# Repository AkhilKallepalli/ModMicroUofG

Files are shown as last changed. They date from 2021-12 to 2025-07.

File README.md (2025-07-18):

# **ModMicroUofG**

<p align="center">
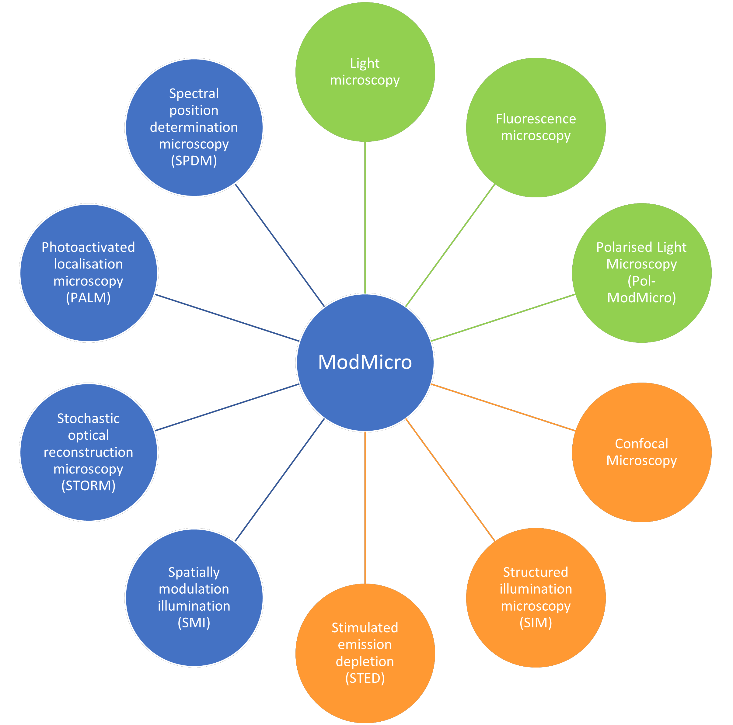
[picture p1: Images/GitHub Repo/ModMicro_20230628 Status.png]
ModMicro Status Update

</p>

**Mod**ular **Micro**scopy is an ongoing project, focusing on building low-cost and accessible hardware for realising standard and complex microscopic techniques. The repository contains all the files, modifications and updates.

<p align="center">
Work in Progress Logo
</p> 

---

# **Contents**

## **Phase 1: [OpenFlexure microscope](https://openflexure.org/) and machine learning-enhanced classification** 

The research adopts the OpenFlexure Delta Stage microscope (https://openflexure.org/) that allows motorised control and maximum stability of the samples when imaging. A Raspberry Pi camera is used for imaging the samples in a transmission-based illumination setup. The imaging data collected is catalogued and organised for classification using TensorFlow. Using visual interpretation, we have created subsets from amongst the samples to experiment for the best classification results. We found that by removing similar samples, the categorical accuracy achieved was 99.9% and 99.59% for the training and testing sets. Our research shows evidence of the efficacy of open source tools and methods. Future approaches will use improved resolution images for classification and other modalities of microscopy will be realised based on the OpenFlexure microscope. TEST

**Important Links**: 
- [GitHub](https://github.com/AkhilKallepalli/ModMicroUofG/tree/260d3f88ae4605c2fc237944587647aae78d652a/Phase%201%20(Microscope%20and%20ML))
- [OPEN-BIOset Dataset](http://dx.doi.org/10.5525/gla.researchdata.1149)
- SPIE Conference Proceeding: [Modular light sources for microscopy and beyond (ModLight)](https://doi.org/10.1117/12.2599435)

---
---

## **ModLight: Modular light sources** 

Modular light (ModLight) sources can be integrated into complex systems for microscopy, medical imaging, remote sensing, and so many more. Motivated by the need for affordable and open-access alternatives that are globally relevant, we have designed and shared light devices that use simple, off-the-shelf components. Red, green, blue, white and near-infrared LEDs are combined using mirrors and X-Cube prisms in novel devices. This modular nature allows portability and mounting flexibility. The ModLight suite can be used with any optical system that requires single- or multi-wavelength illumination such as bright-field and epifluorescence microscopes.

**Important Links**: 
- [Zenodo](https://zenodo.org/record/7385903)
- HardwareX Paper: [Modular light sources for microscopy and beyond (ModLight)](https://doi.org/10.1016/j.ohx.2022.e00385)

***NOTE**: Files of the same version as on Zenodo and HardwareX paper availble through this [GitHub Folder](https://github.com/AkhilKallepalli/ModMicroUofG/tree/c88cae8ca496235c1b51023b1f2a8044d0d7d9a2/ModLight).* 

---
---

## **Phase 2: Epifluorescence Microscopy** 

In collaboration with [Dr Jonathan Taylor](https://www.gla.ac.uk/schools/physics/staff/jonathantaylor/), the research led by Mr Robert Archibald investigated comparing a modular epifluorescence microscope with a standard Nikon Ti-Eclipse microscope. The results have shown that our results match the resolution and image sharpness as compared to a proprietary microscope, that latter costing many orders of the 3D printed microscopy system. 

### ***Hardware*** 
The original [OpenFlexure microscope](https://openflexure.org/) is adopted as the template, leveraging the flexures and their stability. Our contributions include a modified version of the epifluorescence setup to enhance access to the optics, introduce modular attachments and in-house built [ModLight](https://doi.org/10.1016/j.ohx.2022.e00385) sources to increase the spectral fidelity of a single system. 

### ***Sharpening Algorithm*** 
Image prossessing techniques are an essential step in data analysis, especially so when the image quality is degraded. This paper presents an iterative sharpening algorithm designed for use on the OpenFlexure Microscope, to bring z-stack images back into focus. Three different sharpness metrics are evaluated and the data needed to process these images, and establish the highest quality after image acquisition is available [here](https://github.com/AkhilKallepalli/ModMicroUofG/tree/a79b8e51664f305bbde2d7f3cc1418ee8469735c/Phase%202%20(Epifluorescence%20Microscope)/Sharpening%20algorithm). 

**Important Links**: 
- [GitHub](https://github.com/AkhilKallepalli/ModMicroUofG/tree/260d3f88ae4605c2fc237944587647aae78d652a/Phase%202%20(Epifluorescence%20Microscope))
- Research article: **Under Preparation**

---
---

## **Phase 3: Confocal Microscopy** 

<p align="center">
Work in Progress Logo
</p> 

---
---

## **Phase 4: Structured Illumination Microscopy** 

<p align="center">
Work in Progress Logo
</p> 

---
---

<p align="center">
     
</p>

---
---

## *Contact Information*

*For further details, discussions and collaborations, please contact Dr Akhil Kallepalli*\
**Email**: Akhil.Kallepalli@glasgow.ac.uk

*To learn more about our research, check out the lab website*\
**Website**: https://kallepallilab.com

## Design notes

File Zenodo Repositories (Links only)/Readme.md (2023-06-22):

# Zenodo Repositories 

Our research is currently distributed across Git and Zenodo repositories. While the Git repositories are accessible on [Github](https://github.com/AkhilKallepalli/ModMicroUofG), three repositories currently reside on Zenodo: 

- [**Biophotonics for All: Light Transport through Tissue**](https://zenodo.org/record/7876304)
- [**Pol-ModMicro**](https://zenodo.org/record/7837389)
- [**Modular light sources for microscopy and beyond (ModLight)**](https://zenodo.org/record/7385903)

---

## Biophotonics for All: Light transport through tissue

[Repository Access](https://zenodo.org/record/7876304)

This repository includes:

- Design files of electronics, mounts, LED Assembly (from ModLight) and LED mounts 
- Kit overview and LEDs assembly photographs 
- Demonstration Video of the Kit
- Bill of Materials

Biophotonics is becoming increasingly prominent in value and visibility. What was predominantly an advanced field of research is now being included increasingly in undergraduate and postgraduate programmes. To increase biophotonics-related STEM awareness, we developed simple and inexpensive LEDs and a camera set-up that allows visualising the blood vessels beneath the skin. The kit uses inexpensive blue, green, red and near-infrared LEDs to show the absorption of shorter wavelengths and transmission in the longer wavelengths in the finger. As an outreach and educational tool, this kit will illustrate the potential of using light for diagnostics.

<p align="center">
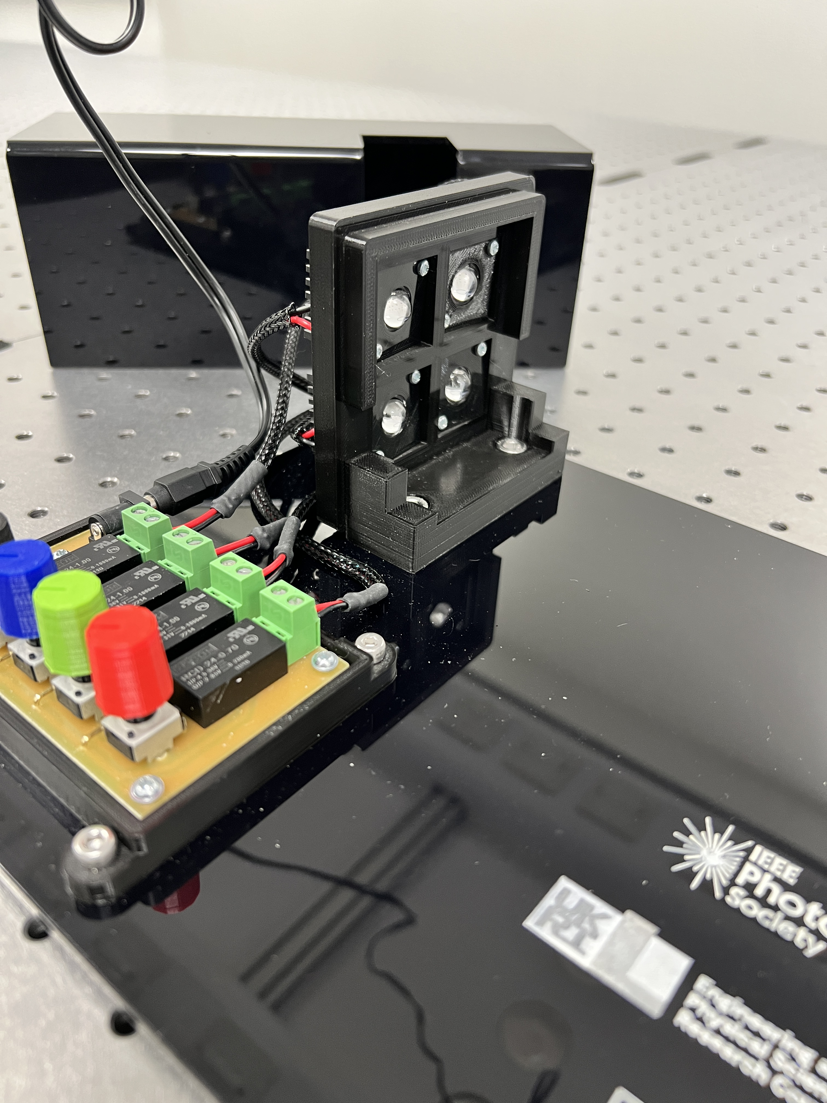
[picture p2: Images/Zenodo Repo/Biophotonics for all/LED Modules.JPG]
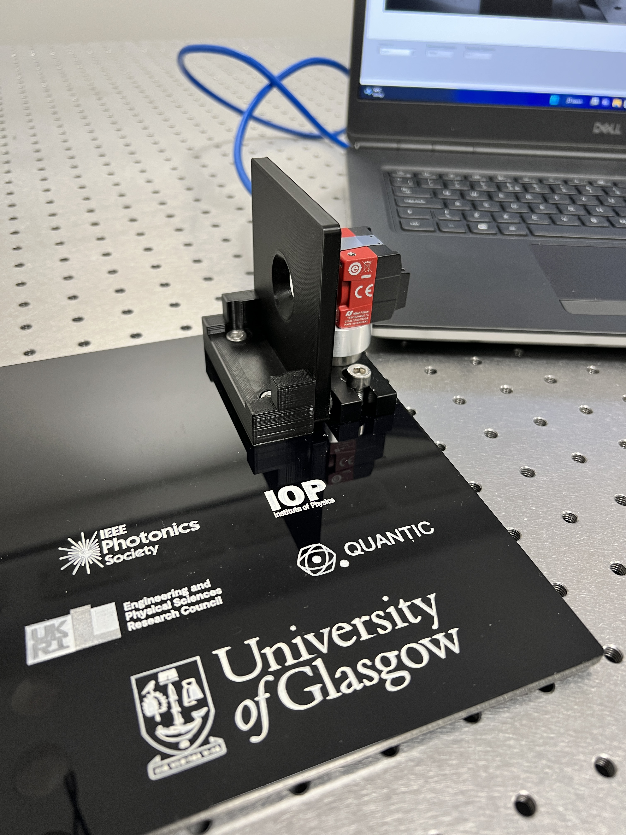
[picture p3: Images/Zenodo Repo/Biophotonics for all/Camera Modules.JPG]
 
</p>

<p align="center">

</p>

---

## Polarised light modular microscopy (Pol-ModMicro) for identifying hemozoin crystals in Plasmodium

[Repository Access](https://zenodo.org/record/7837389)

In this repository, you will find all the files needed to recreate the Pol-ModMicro system. These include: 

- Unmodified OpenFlexure files; as used in the system. 
- Modified/Updated Components to allow ModLight integration
- OpenFlexure Nano Motor Controller files
- Bill of Materials

Plasmodium spp. are the protozoan parasites responsible for malaria. Plasmodium spp. synthesise a biocrystal, hemozoin, which can be observed under cross-polarised light. These birefringent crystals can be seen due to different refractive indices of the hemozoin crystal and red blood cells. Here, we present a polarised light modular microscopy (Pol-ModMicro) solution, complete with illumination sources and a robust imaging system to capture birefringence and identify the parasites. We achieve this by combining ModLight light sources with bespoke components designed for the OpenFlexure microscope to image blood smears. Further, a simple and robust algorithm capable of enhancing birefringence is presented. This solution provides image quality that is comparable to a substantially more expensive proprietary microscope. 

<p align="center">
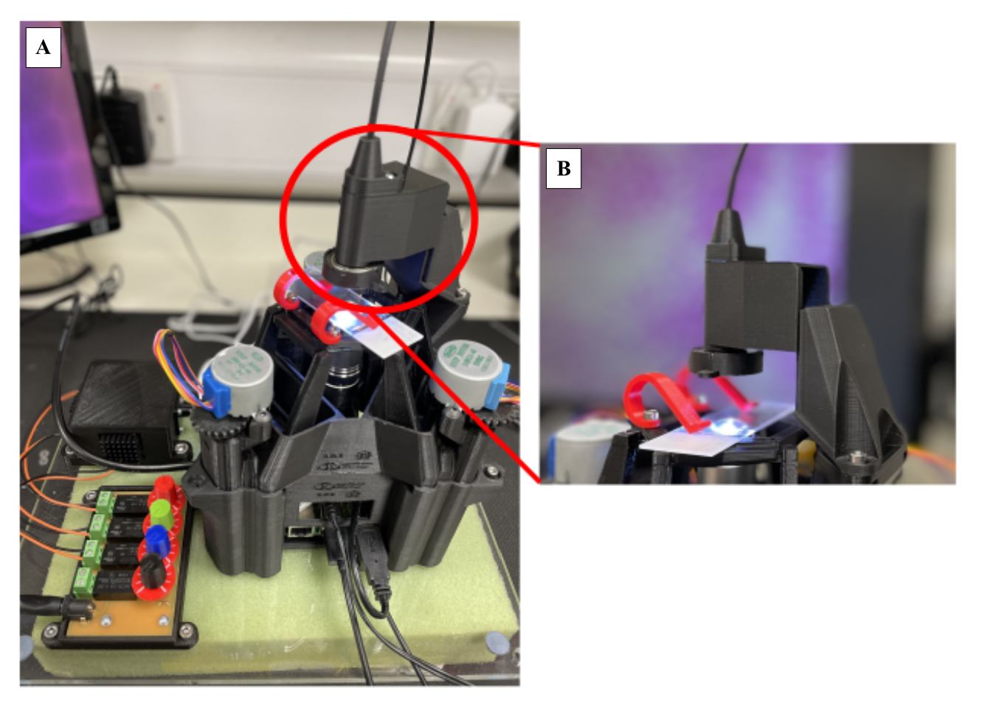
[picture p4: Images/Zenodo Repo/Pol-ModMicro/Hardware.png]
 
</p>

---

## Modular Light Sources for Microscopy and Beyond (ModLight)

[Repository Access](https://zenodo.org/record/7385903)

***NOTE**: Files of the same version as on Zenodo and HardwareX paper availble through this [GitHub Folder](https://github.com/AkhilKallepalli/ModMicroUofG/tree/c88cae8ca496235c1b51023b1f2a8044d0d7d9a2/ModLight).* 

Modular light (ModLight) sources can be integrated into complex systems for microscopy, medical imaging, remote sensing, and so many more. Motivated by the need for affordable and open-access alternatives that are globally relevant, we have designed and shared light devices that use simple, off-the-shelf components. Red, green, blue, white and near-infrared LEDs are combined using mirrors and X-Cube prisms in novel devices. This modular nature allows portability and mounting flexibility. The ModLight suite can be used with any optical system that requires single- or multi-wavelength illumination such as bright-field and epifluorescence microscopes.

<p align="center">
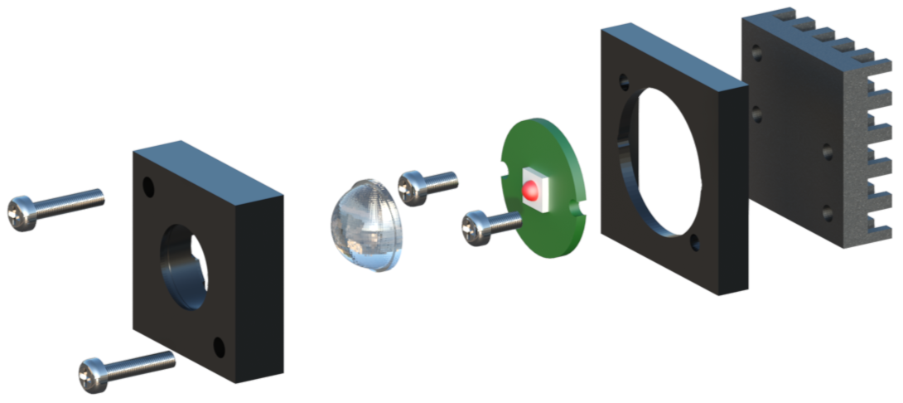
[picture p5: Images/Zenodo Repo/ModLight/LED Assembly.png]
  
</p>

<p align="center">
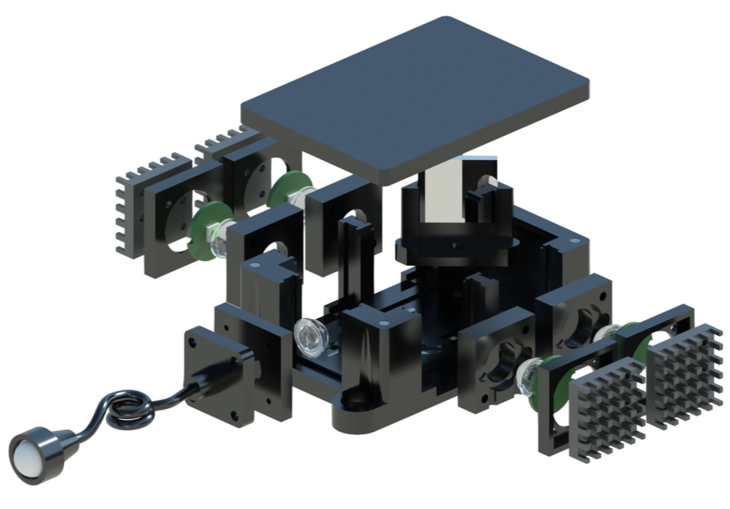
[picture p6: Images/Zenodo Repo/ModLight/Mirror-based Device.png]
 
</p>

<p align="center">
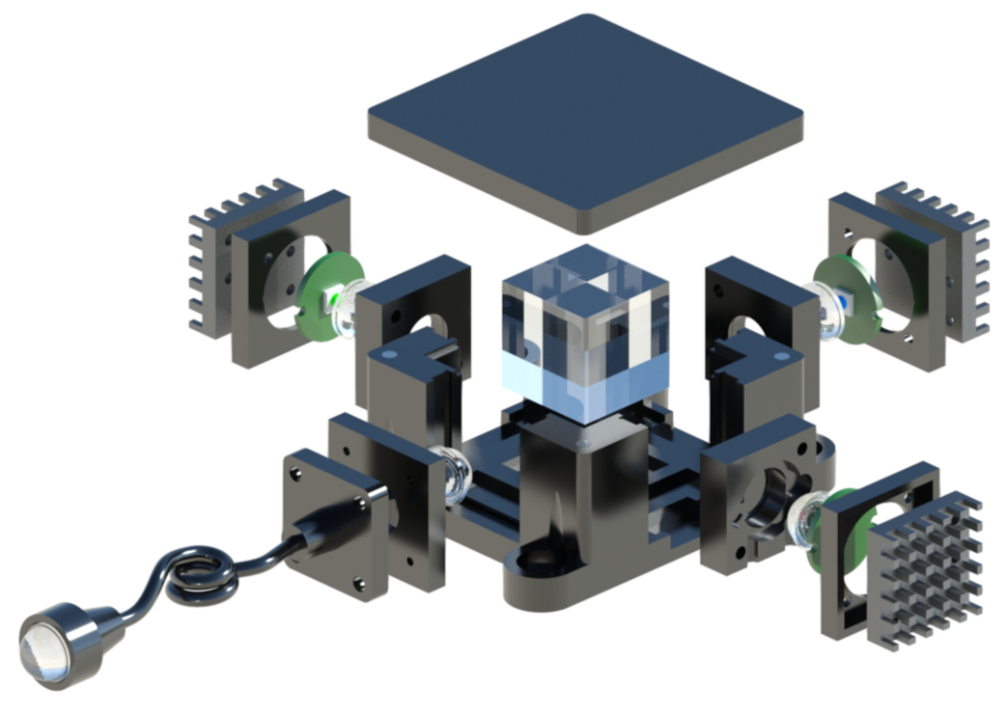
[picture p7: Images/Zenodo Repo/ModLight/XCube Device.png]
 
</p>

<p align="center">
 
</p>

---

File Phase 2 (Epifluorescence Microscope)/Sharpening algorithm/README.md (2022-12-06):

# Z-stack Image Sharpening Algorithm

---

## **Contact Information**

For further details on the algorithm, please contact Ms Harriet Bishop.\
Email: hattiebishop2@gmail.com\
LinkedIn: www.linkedin.com/in/harrietbishop

---

## **Contents**

Provided is a jupyter notebook (.ipynb) file containing an algorithm which sharpens z-stack images as well as the sample data used to test and build the algorithm. 

**The Algorithm:** The algorithm takes each image and sharpens it using various low pass filters. It then selects the optimal image by comparing the peaks in the pixel intensity produced when plotting a line across a prominent feature in the image.  It compares the full width half maximum of the images sharpened by each filter and finds the narrowest (and thus sharpest) one. The algorithm returns the optimized n value which relates to the most suitable low pass filter, of the form np.ones((n,n),np.float32)/(n^2) as well as the images sharpened using this filter. 

**Sample Data:** The sample data provided is a set of z-stack images of an Onion Epidermis slide, taken using the 3D printed OpenFlexure Microscope. The images depict different layers of the onion sample, with 200nm between each plane in the z-direction. The first half of the images (0-48) have been removed due to significant drift in the x-y axis. The starting image, Image 49, is the sharpest image in the stack having been taken at the focal point. The following images are increasingly blurred. Passing this dataset through the algorithm should return an n value of 5 along with a before and after of each image. 

---

## **Motivation**

Z-stack images are taken by adjusting the distance between the sample and the collection optics to focus on different layers of the image. As the sample is moved away from the focal plane, the image becomes increasingly blurred due to out of focus light reaching the collection optics. This algorithm provides a solution to partially restore these blurred images by removing low-frequency regions in the image, extracted using a low pass filter. Different sized filters are appropriate for different images, and this algorithm aims to find and apply the most appropriate filter given a set of images. 

---

## **User Inputs**

The algorithm must be provided with the below listed inputs. 

**directory:** The path to the folder with which the images are located.\
For example: *directory = '/Users/harrietbishop/My Project/Images/OnionEpidermis'*

**x1,y1,x2,y2:** The pixel coordinates plotting a line from A(x1,y1) to B(x2,y2). For best results, the line should be plotted perpendicular to a feature in the image to obtain a clear peak in intensity for analysis. Be aware that the values of y will be reversed as they correspond to the row, which has increasing values as you move more more towards the bottom of the image. It would be wise to plot the z-stack images (using plt.imshow) without removing the axis before choosing these values to help to determine appropriate coordinates. In addition to this, it's important to check that no significant drift has occured in the x-y plane, the plotted line must always cross over the same feature. If drift or sudden displacement has occurred during the stack, temporarily remove these images from the folder before passing through the algorithm. Once an n value is found, the full dataset can then be sharpened again using an optimal nxn low pass filter. \
The coordinates used for the Onion Epidermis dataset are: *x1 = 2447, y1 = 0, x2 = 1000, y2 = 2200*

```python

```

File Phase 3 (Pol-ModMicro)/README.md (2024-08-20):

# **Polarised light modular microscopy (Pol-ModMicro) for hemozoin crystals imaging**

**Important Links**: 
- [Zenodo Repository](https://zenodo.org/record/7837389)
- arXiv: [Polarised light modular microscopy (Pol-ModMicro) for identifying hemozoin crystals in Plasmodium](https://arxiv.org/abs/2304.13739)

---
**Mod**ular **Micro**scopy is an ongoing project, focusing on building low-cost and accessible hardware for realising standard and complex microscopic techniques. 

In collaboration with researchers at universities of Glasgow and Zurich, we developed modified parts for the Openflexure microscope to facilitate imaging with cross-polarised light. The application we pursued and shared through our preprint investigated mapping of hemozoin crystals in *Plasmodium spp.* parasites. 

<p align="center">
 
</p>

---
---
<p align="center">
    
</p>

---
---

## *Contact Information*

*For further details, discussions and collaborations, please contact Dr Akhil Kallepalli*\
**Email**: Akhil.Kallepalli@glasgow.ac.uk

*To learn more about our research, check out the lab website*\
**Website**: https://kallepallilab.com

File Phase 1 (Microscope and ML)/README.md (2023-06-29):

# **ModMicroUofG**

**Important Links**: 
- [GitHub](https://github.com/AkhilKallepalli/ModMicroUofG/tree/260d3f88ae4605c2fc237944587647aae78d652a/Phase%201%20(Microscope%20and%20ML))
- [OPEN-BIOset Dataset](http://dx.doi.org/10.5525/gla.researchdata.1149)
- SPIE Conference Proceeding, [Open-source microscopic solution for classification of biological samples](https://doi.org/10.1117/12.2599435)
---

**Mod**ular **Micro**scopy is an ongoing project, focusing on building low-cost and accessible hardware for realising standard and complex microscopic techniques. In phase 1, our research included building the Openflexure microscope system and investigating its feasibilty for (1) machine learning innovations and (2) feasibility for future applications and innovations. 

- In this phase, we built a standard Openflexure microscope and generated a dataset for machine learning applications. The dataset of brightfield images at high resolution (using x40 and x100 objectives) is openly accessible as the [OPEN-BIOset](http://dx.doi.org/10.5525/gla.researchdata.1149). 

- With this data, we used machine learning algorithms to classify the images with a categorical accuracy of 99.59% (testing data). 

The hardware used in the research uses the [OpenFlexure](https://openflexure.org/) microscope, with the [Delta Stage](https://openflexure.org/projects/deltastage/) variant. 

<p align="center">

</p>

---
---

<p align="center">
    
</p>

---
---

## *Contact Information*

*For further details, discussions and collaborations, please contact Dr Akhil Kallepalli*\
**Email**: Akhil.Kallepalli@glasgow.ac.uk

*To learn more about our research, check out the lab website*\
**Website**: https://kallepallilab.com

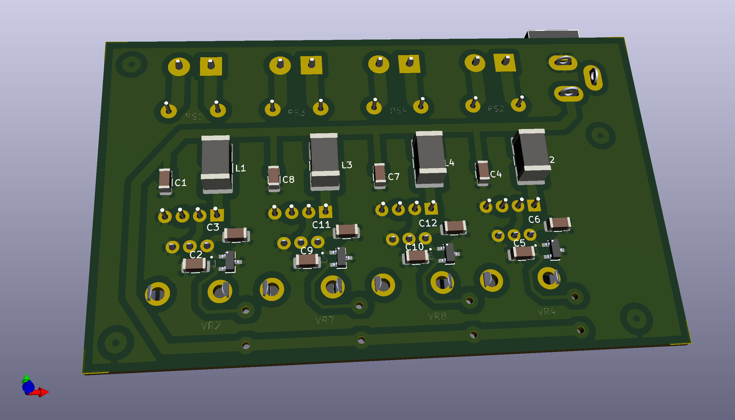
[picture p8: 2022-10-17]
Modular Light Sources (ModLight)/ModLight/Electronics/Images/LED (Quad Control).png

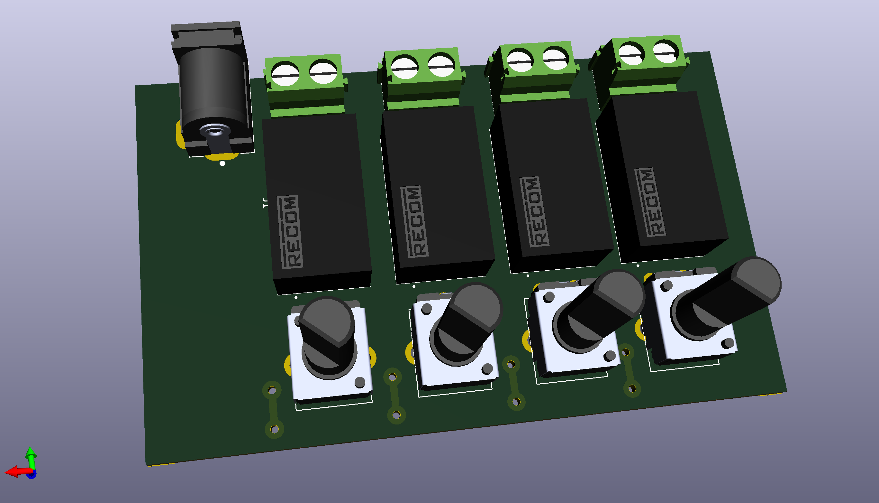
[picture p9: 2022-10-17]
Modular Light Sources (ModLight)/ModLight/Electronics/Images/Top_LED (Quad Control).png

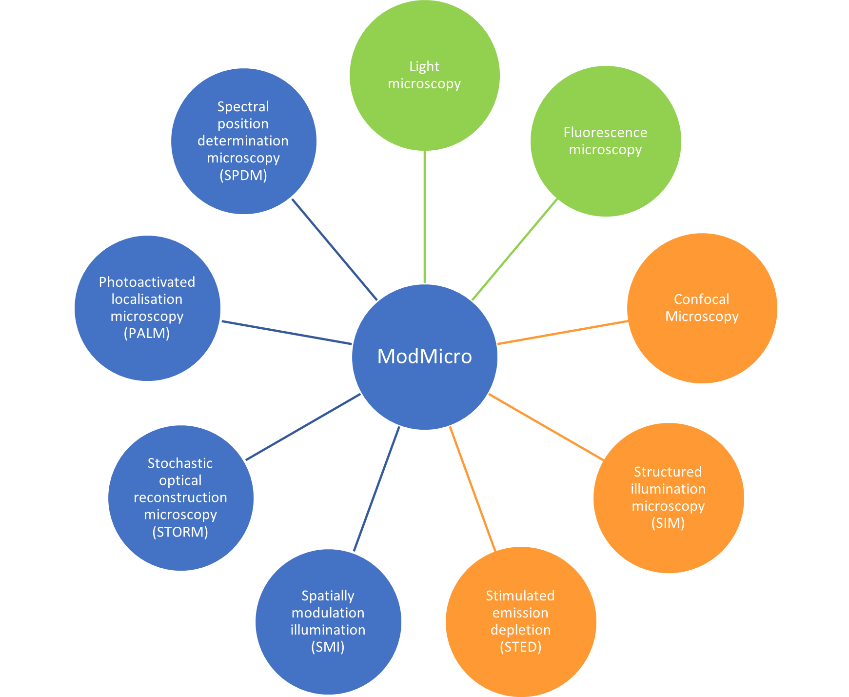
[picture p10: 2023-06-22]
Images/GitHub Repo/ModMicro_20230622 Status.png

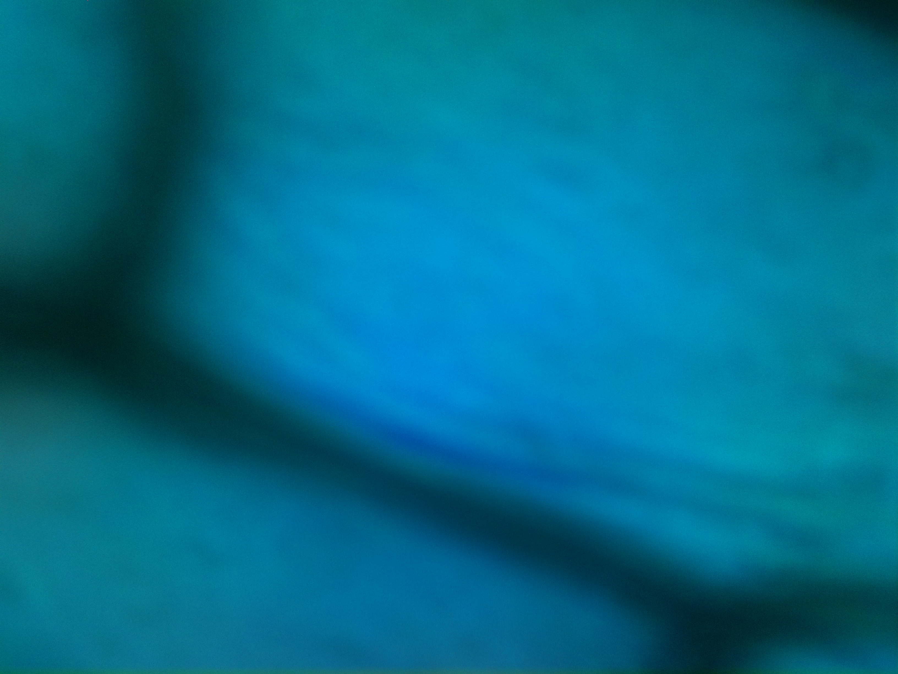
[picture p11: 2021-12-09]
Phase 2 (Epifluorescence Microscope)/Sharpening algorithm/sample_data/OnionEpidermis_200nm_062.jpeg

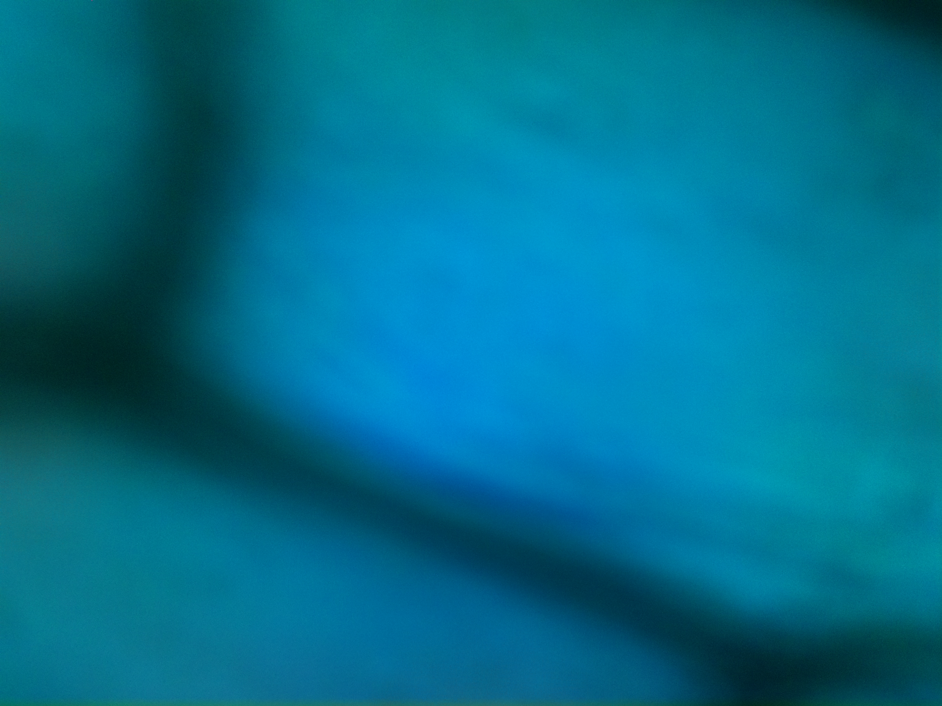
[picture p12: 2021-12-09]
Phase 2 (Epifluorescence Microscope)/Sharpening algorithm/sample_data/OnionEpidermis_200nm_074.jpeg

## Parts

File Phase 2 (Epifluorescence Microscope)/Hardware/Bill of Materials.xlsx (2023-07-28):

Designator (Used in Paper), Quantity Needed | Component/Description | Number | Cost per unit (GBP) Excl. VAT & Delivery | Total Cost (GBP) Excl. VAT & Delivery | Source of Materials
M3x10 mm cap head screws, Required: 10+ | Hex Socket Screw, Cap Head, M3 x 10mm, Stainless Steel A2 (Pack of 100) | 1 | £13.33 | £13.33 | https://uk.farnell.com/tr-fastenings/tr00005751-000/screw-cap-head-hex-m3x10-ss-a2/dp/4156917?st=m3%20cap%20head%20screws
M3x25 mm hex head screw, Required: 3 | Set Screw, M10, 25 mm, Stainless Steel, Hex Head (Pack of 10) | 1 | £4.06 | £4.06 | https://uk.farnell.com/duratool/d01993/set-screw-hex-m10-x-25mm-pk10/dp/2444394?st=25%20hex%20head%20screw
M3 nut, Required: 10+ | Nut, Hex, M3, Steel, Bright Zinc Plated (Pack of 100) | 1 | £1.40 | £1.40 | https://uk.farnell.com/tr-fastenings/m3-hfst-z100/nut-full-steel-bzp-m3-pk100/dp/1419447?st=M3%20nut
M3 washer, Required: 10+ | Washer, Plain, Steel, M3 (Pack of 100) | 1 | £1.31 | £1.31 | https://uk.farnell.com/duratool/wash3/washer-steel-m3-pk100/dp/1377496?st=m3%20washer
5x3 mm magnets, Required: 8 | 5mm x 3mm small magnet (Pack of 50) | 1 | £4.99 | £4.99 | https://www.amazon.co.uk/FINDMAG-Fridge-Magnets-Strong-Whiteboard/dp/B0BTLPTRSG?sp_csd=d2lkZ2V0TmFtZT1zcF9hdGY
M4x6 mm button head screws, Required: 6 | Socket Screw, Button Head Hex Socket, Steel, 6 mm, M4 (Pack of 100) | 1 | £9.08 | £9.08 | https://uk.farnell.com/tr-fastenings/m46-bh10mcs100/screw-socket-butt-m4x6-pk100/dp/1420686?st=m4%20button%20head%20screws
O-ring, Required: 3 | 2mm Section 30mm Bore VITON Rubber O-Rings (Pack of 100) | 1 | £32.50 | £32.50 | https://simplybearings.co.uk/shop/p513396/2mm-Section-30mm-Bore-VITON-Rubber-O-Rings/product_info.html
M2.2x6.5 mm self tapping screws, Required: 2 | Pozi Pan Self Tapping Screw (AB) No.2 x 6.5mm in A2 Stainless - DIN 7981 (pack of 40) | 1 | £2.12 | £2.12 | https://www.westfieldfasteners.co.uk/Self-Tapping-Screws/Pozi-Pan-Self-Tapping-Screw-AB-No.2x6.5-A2-Stainless.html
Objective Lens, Required: 1 | RMS10X - 10X Olympus Plan Achromat Objective, 0.25 NA, 10.6 mm WD | 1 | £308.63 | £308.63 | https://www.thorlabs.com/thorproduct.cfm?partnumber=RMS10X
Dichroic Mirror, Required: 1 | 25 x 36 mm Longpass Dichroic Mirror, 505nm Cut-On | 1 | £205.27 | £205.27 | https://www.thorlabs.com/thorproduct.cfm?partnumber=DMLP505R
Emission Filter, Required: 1 | Emission Filter, CWL=535nm BW+22nm | 1 | £207.89 | £207.89 | https://www.thorlabs.com/thorproduct.cfm?partnumber=MF535-22
Tube Lens, Required: 1 | f=125mm, 1" Achromatic Doublet, ARC:400-700nm | 1 | £65.51 | £65.51 | https://www.thorlabs.com/thorproduct.cfm?partnumber=AC254-125-A
Condenser Lens, Required: 2 | optical PMMA plano convex lens diameter 13mm focal length 5mm (Pack of 100) | 1 | £21.78 | £21.78 | https://www.aliexpress.com/w/wholesale-13mm-5mm-pmma-lens.html
Mirror, Required: 1 | 25 x 35 mm Enhanced Aluminium Mirror | 1 | £21.25 | £21.25 | https://www.edmundoptics.co.uk/p/25-x-35mm-enhanced-aluminum-4-6lambda-mirror/5361/
Raspbery Pi, Required: 1 | Raspberry Pi 3 Model B+ 1 Quad Core 1.4GHz 1GB RAM WiFi & Bluetooth | 1 | £36.64 | £36.64 | https://www.rapidonline.com/raspberry-pi-3-model-b-1-quad-core-1-4ghz-1gb-ram-wifi-bluetooth-75-1005?src=raspberrypi
Raspberry Pi power supply, Required: 1 | 2mm Section 30mm Bore VITON Rubber O-Rings (pack of 10) | 1 | £7.04 | £7.04 | https://simplybearings.co.uk/shop/p513396/2mm-Section-30mm-Bore-VITON-Rubber-O-Rings/product_info.html
Raspbery Pi camera v2, Required: 1 | Daughter Board, Raspberry Pi Camera Board, Version 2, Sony IMX219 8-Megapixel Sensor | 1 | £22.00 | £22.00 | https://uk.farnell.com/raspberry-pi/rpi-8mp-camera-board/raspberry-pi-camera-board-v2/dp/3677845?CMP=KNC-GUK-GEN-KWL-CLM-CARTABAN-10OFF&mckv=_dc|pcrid|626593324211|kword||match||plid||slid||product||pgrid|140532649805|ptaid|aud-140011313109:dsa-1814079156442|&gclid=CjwKCAjwov6hBhBsEiwAvrvN6O-aklIc29pCxqZq4iy2P648nNDc3e5c-JIW7EuwekTS0EeazyuRuRoCW4YQAvD_BwE
MICROUSB, Required: 1 | USB Connector, Micro USB Type B, USB 2.0, Receptacle, 5 Ways, Surface Mount, Right Angle | 1 | £5.79 | £5.79 | https://uk.farnell.com/amp-te-connectivity/1981568-1/micro-usb-conn-2-0-type-b-rcpt/dp/2751670
USB cable, Required: 1 | CBL-UA-P5-1 | 1 | £2.18 | £2.18 | https://www.digikey.co.uk/short/z1424b
28BYJ-48 micro geared stepper motor, Required: 3 | ELEGOO 5 sets 28BYJ-48 5V Stepper Motor + ULN2003 Motor Driver Board for Arduino | 1 | £17.99 | £17.99 | https://www.amazon.co.uk/Elegoo-28BYJ-48-Stepper-ULN2003-Arduino/dp/B01LXT5740
1" Slip Ring, Required: 1 | C1RC/M - Slip Ring for Ø1" (Ø25.4 mm) Components, M4 Tap | 1 | £22.27 | £22.27 | https://www.thorlabs.com/thorproduct.cfm?partnumber=C1RC/M
Optical Post, Required: 1 | TR50/M - Ø12.7 mm Optical Post, SS, M4 Setscrew, M6 Tap, L = 50 mm | 1 | £4.43 | £4.43 | https://www.thorlabs.com/thorproduct.cfm?partnumber=TR50/M
Pedestal Post Holder, Required: 1 | PH1.5E - Ø1/2" Pedestal Post Holder, Spring-Loaded Hex-Locking Thumbscrew, L=1.69" | 1 | £20.53 | £20.53 | https://www.thorlabs.com/thorproduct.cfm?partnumber=PH1.5E#ad-image-0
Link to original PCB+Arduino Nano setup:
https://kitspace.org/boards/github.com/rwb27/openflexure_nano_motor_controller/
Diagram showing fitting and assemply:
https://kitspace.org/interactive_bom/?github.com/rwb27/openflexure_nano_motor_controller
Link to ModLight:
https://doi.org/10.1016/j.ohx.2022.e00385

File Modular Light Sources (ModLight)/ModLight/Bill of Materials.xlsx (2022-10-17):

Designator (Used in Paper) | Component/Description | Number | Cost per unit (GBP) Excl. VAT & Delivery | Total Cost (GBP) Excl. VAT & Delivery | Source of Materials | Material Type
HS | Heatsink | 7 | £1.38 | £9.66 | https://uk.rs-online.com/web/p/heatsinks/6744743/ | Aluminium
LED-IR-950 | IR (LED) at 950 nm | 2 | £2.86 | £5.72 | https://uk.rs-online.com/web/p/ir-leds/7781383/ | Semiconductor
LED-IR-860 | IR (LED) at 860 nm | 2 | £3.26 | £6.52 | https://uk.rs-online.com/web/p/ir-leds/7531567 | Semiconductor
LED-R | Red LED | 2 | £1.23 | £2.46 | https://uk.farnell.com/cree/xpebrd-l1-0000-00801/led-smd-xlamp-xpe-e-red-73-9lm/dp/2335108?ost=2335108 | Semiconductor
LED-G | Green LED | 2 | £1.85 | £3.70 | https://uk.farnell.com/cree/xpegrn-l1-r250-00c01/xp-color/dp/1727688?st=green%20led | Semiconductor
LED-B | Blue LED | 2 | £3.39 | £6.78 | https://uk.farnell.com/lumileds/lxml-pb01-0023/led-luxeon-rebel-blue-23lm/dp/1376625?ost=1376625 | Semiconductor
LED-W | White LED | 1 | £2.58 | £2.58 | https://uk.farnell.com/lumileds/lxml-pwc2/led-rebel-es-high-power/dp/1834323?ost=1834323 | Semiconductor
PMMA-f5 | 5 mm focal length lenses (pack of 100) | 1 | £46.50 | £46.50 | https://www.amazon.co.uk/dp/B08S7LNJLY?ref_=cm_sw_r_cp_ud_dp_BABGMY8FSQF3DZTDERVY | PMMA
BB-5mm | Ball bearing (5 mm diameter, pack of 100) | 1 | £8.49 | £8.49 | https://www.amazon.co.uk/dp/B07YKLMB5V?ref_=cm_sw_r_cp_ud_dp_3G5WJW27TZEXJQ9M6PX6 | Stainless Steel
M-6x3 | Magnets (6mm x 3 mm, Pack of 40) | 1 | £4.99 | £4.99 | https://www.amazon.co.uk/dp/B07GFK5XFC?ref_=cm_sw_r_cp_ud_dp_GPY2P2ZFT0J40YT7G5T0 | Nickel
M-3x2 | Magnets (3mm x 2 mm, Pack of 50) | 1 | £3.24 | £3.24 | https://www.amazon.co.uk/dp/B00YYJDYRY?ref_=cm_sw_r_cp_ud_dp_XTTYDGVNGFVDCTWSYJQH | Nickel
P-2x8 | Dowel Pins (2mm x 8 mm, Pack of 20) | 1 | £3.99 | £3.99 | https://www.amazon.co.uk/dp/B07VQ4S16J?ref_=cm_sw_r_cp_ud_dp_YHF8ANCNDGQNF6DNFX45 | Stainless Steel
S-M2.5-6 | M2.5 Screws (6 mm length, Pack of 100) | 1 | £1.15 | £1.15 | https://uk.farnell.com/multicomp-pro/mp006578/screw-pan-head-pozidriv-m2-5-6mm/dp/3666777?st=m2.5%20screw | Carbon Steel, Zinc
S-M2.5-12 | M2.5 Screws (12 mm length, Pack of 100) | 1 | £1.27 | £1.27 | https://uk.farnell.com/multicomp-pro/mp006579/screw-pan-head-pozidriv-m2-5-12mm/dp/3666778?st=m2.5%20screw | Carbon Steel, Zinc
Mirror | Mirror (25 MP 25, 3 mm thickness) | 1 | £22.39 | £22.39 | https://www.comaroptics.com/components/plano-optics/mirrors/general-purpose-plane | Ion-plated Silver
Xcube | X-Cubes (25x25x25 mm) | 1 | £10.27 | £10.27 | https://www.aliexpress.com/item/4000066481806.html | Glass
EW-B | Electrical Cables (Black, Reel of 25 m) | 1 | £34.19 | £34.19 | https://uk.farnell.com/brand-rex/spc00448a002-25m/wire-ptfe-b-black-19-0-15mm-25m/dp/1184082 | Copper
EW-R | Electrical Cables (Red, Reel of 25 m) | 1 | £34.19 | £34.19 | https://uk.farnell.com/brand-rex/spc00448a001-25m/wire-ptfe-b-red-19-0-15mm-25m/dp/1184087 | Copper
Fibre | Light Guide (2000μm with 1 Fiber, Optical Grade Plastic Light Guide, minimum 10 ft) | 1 | £4.06 | £4.06 | https://www.edmundoptics.co.uk/p/2000mum-with-1-fiber-optical-grade-plastic-light-guide/81/ | Glass with Black Polyethylene Jacket
LED-IC | LED Driver | 7 | £15.24 | £106.68 | https://uk.rs-online.com/web/p/led-driver-ics/6689870 | Semiconductor
LED-P | Potentiometers | 7 | £0.53 | £3.69 | https://uk.farnell.com/bourns/ptv09a-4225f-b103/potentiometer-10k-0-05w-20-panel/dp/2663537?ost=2663537 | Semiconductor
VR1, VR3, VR5 & VR6 | 5V Regulator (TLV76050DBZT) | 4 | £0.91 | £3.64 | https://uk.farnell.com/texas-instruments/tlv76050dbzt/ldo-fixed-5v-0-1a-sot-23-3/dp/3122390?st=tlv76050dbzt | Semiconductor
L1, L2, L3 & L4 | 47uH inductor | 4 | £0.60 | £2.40 | https://uk.farnell.com/bourns/sdr0603-470kl/inductor-47uh-10-0-52a-smd/dp/2328780
C1, C4, C7, C8 | 2.2uF capacitor (multiples of 5) | 5 | £0.42 | £2.10 | https://uk.farnell.com/multicomp/mc1206f225z250ct/cap-2-2-f-25v-y5v-1206/dp/1759451
C2, C3, C5, C6, C9, C10, C11, C12 | 0.1uF capacitor (multiples of 5) | 8 | £0.19 | £1.52 | https://uk.farnell.com/multicomp/mcsh31b104k100ct/cap-0-1-f-10v-10-x7r-1206/dp/1856599
Note: The parts listed are considering both sources are being built. If only one of the sources are required, choose appropriately.

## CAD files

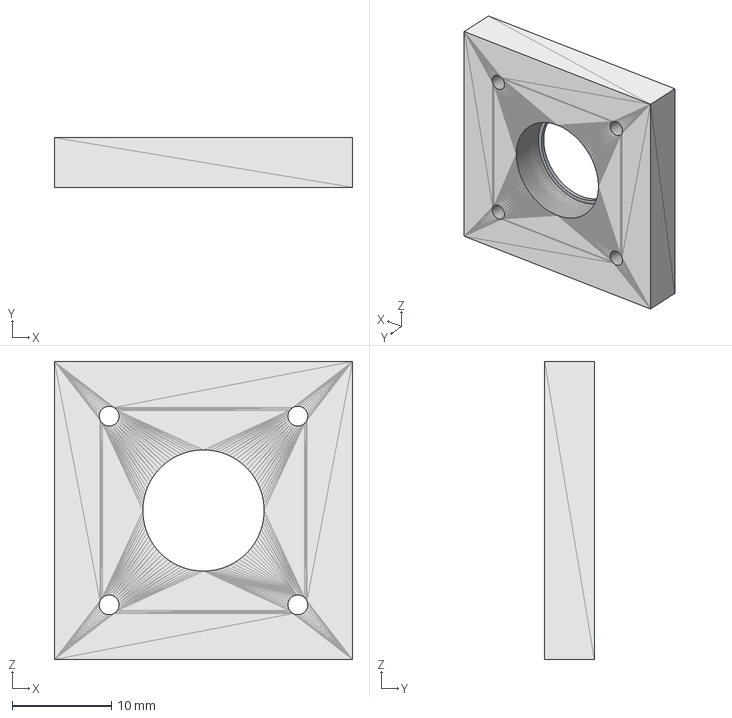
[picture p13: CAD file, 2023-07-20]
Modular Light Sources (ModLight)/ModLight/Common Files/STEP/Fibre Mount_STEP.step
30.0 x 5.00 x 30.0 mm

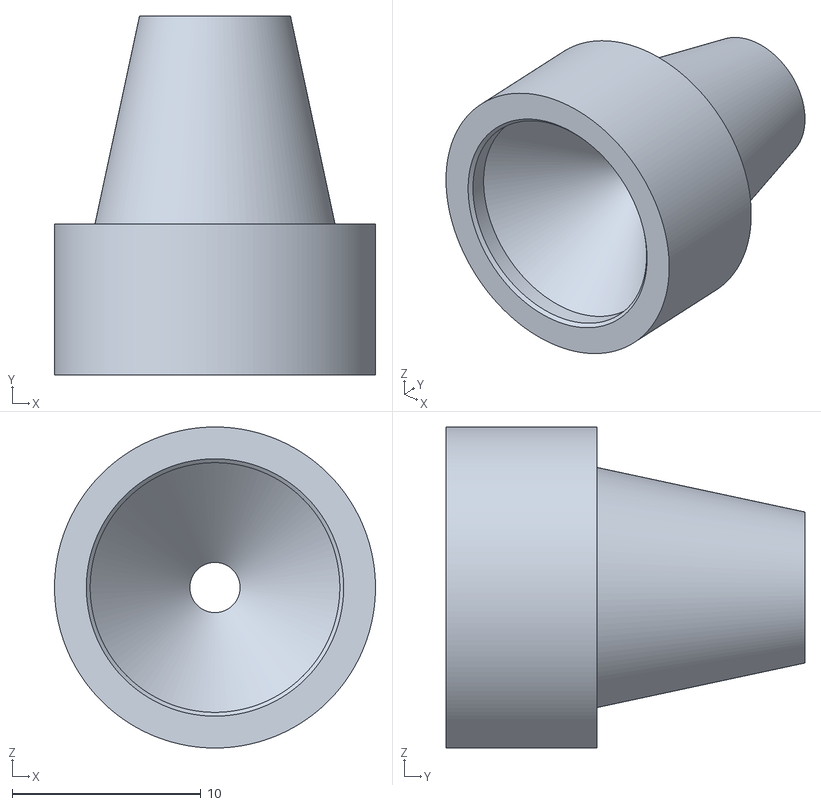
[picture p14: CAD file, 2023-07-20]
Modular Light Sources (ModLight)/ModLight/Common Files/STL/Fibre Collimator_STL.stl
17.0 x 19.0 x 17.0

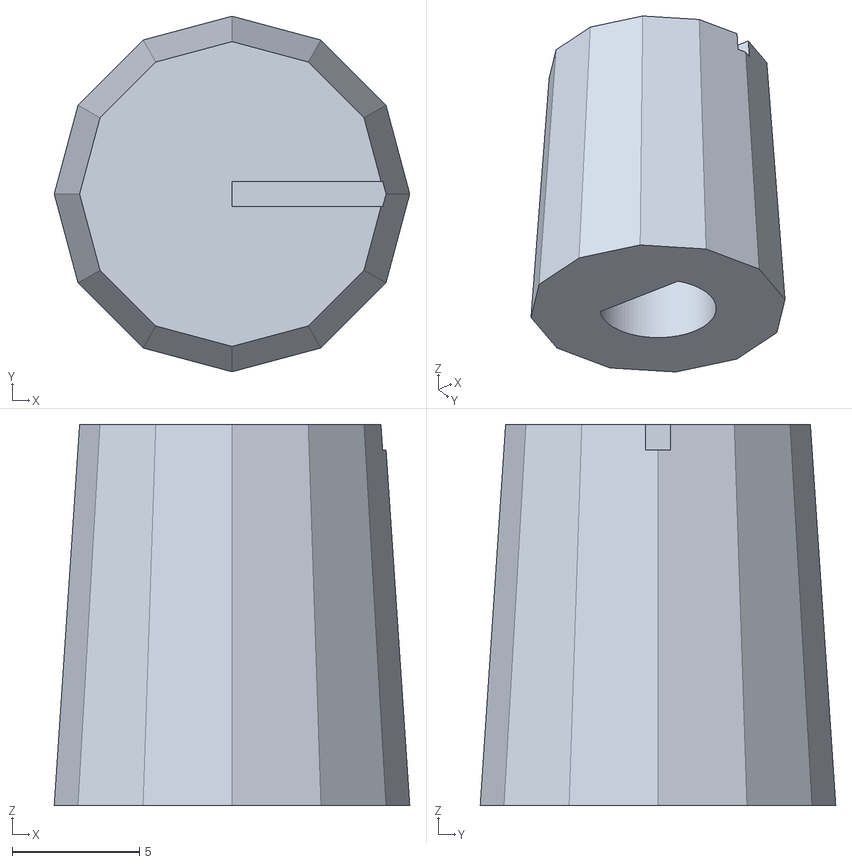
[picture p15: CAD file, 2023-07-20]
Modular Light Sources (ModLight)/ModLight/Electronics/STL/Dial_STL.stl
14.0 x 14.0 x 15.0

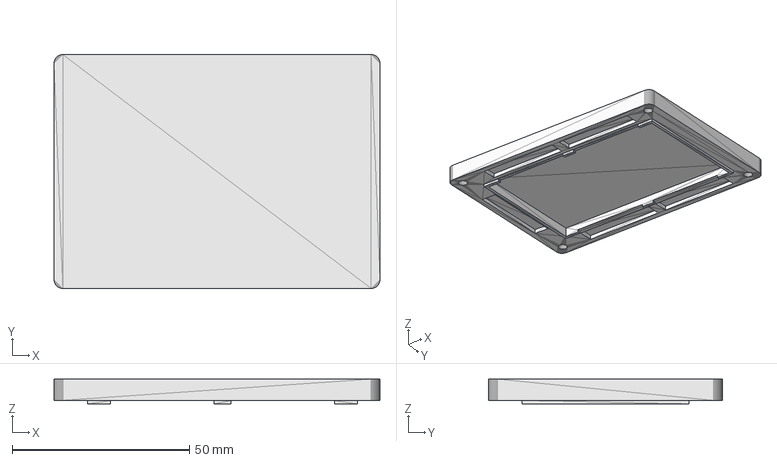
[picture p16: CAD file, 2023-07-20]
Modular Light Sources (ModLight)/ModLight/ModLight_Mirror/STEP/MLight Box (Lid)_STEP.step
92.0 x 66.0 x 7.00 mm

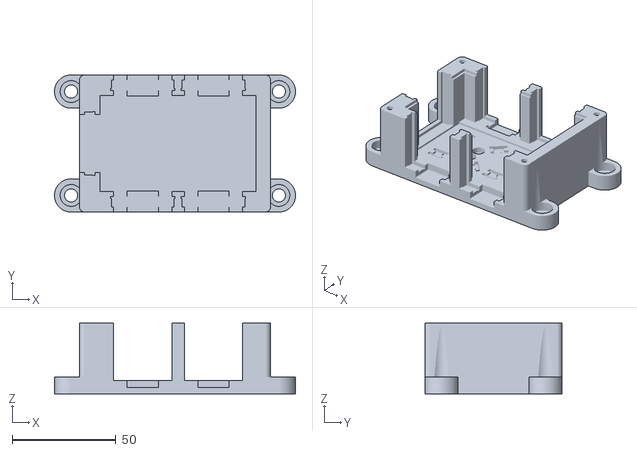
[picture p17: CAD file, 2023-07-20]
Modular Light Sources (ModLight)/ModLight/ModLight_Mirror/STL/MLight Box_STL.stl
116.0 x 66.0 x 34.0

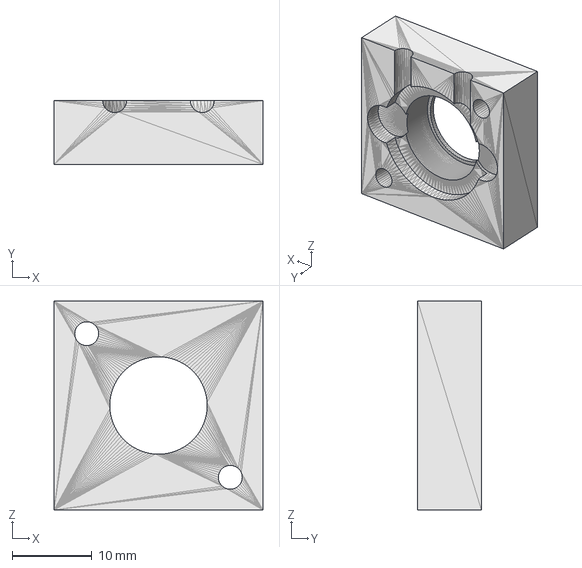
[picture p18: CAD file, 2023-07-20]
Modular Light Sources (ModLight)/ModLight/ModLight_XCube/STEP/XLED Spacer_STEP.step
26.2 x 8.00 x 26.2 mm

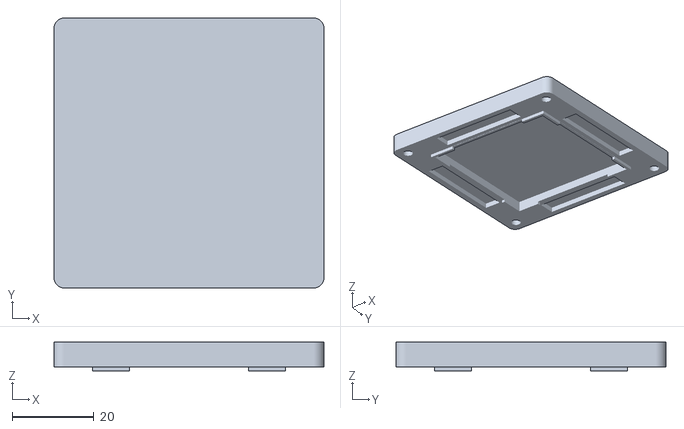
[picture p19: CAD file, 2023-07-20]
Modular Light Sources (ModLight)/ModLight/ModLight_XCube/STL/XLight Mixer (Lid)_STL.stl
66.0 x 66.0 x 7.01

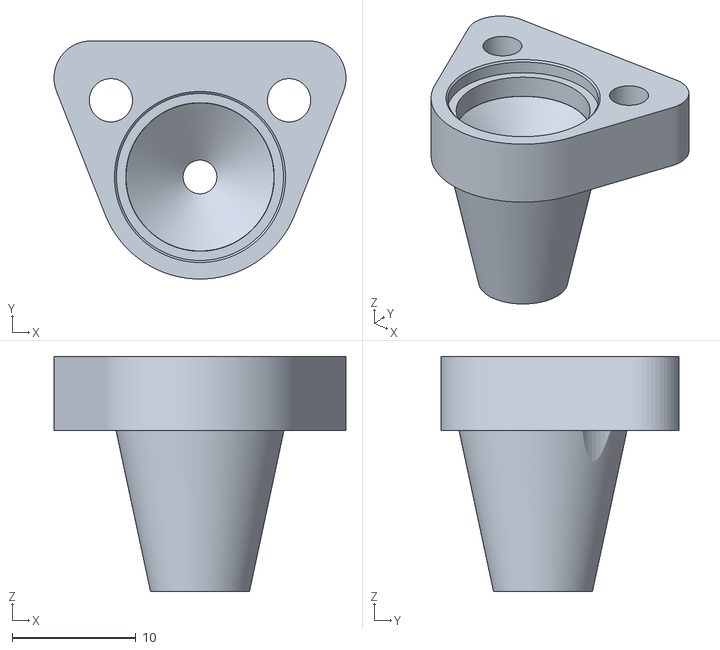
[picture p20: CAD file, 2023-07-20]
Modular Light Sources (ModLight)/ModLight/OpenFlexure_Modified/Fibre_Holder_Modified.stl
23.6 x 19.2 x 19.0

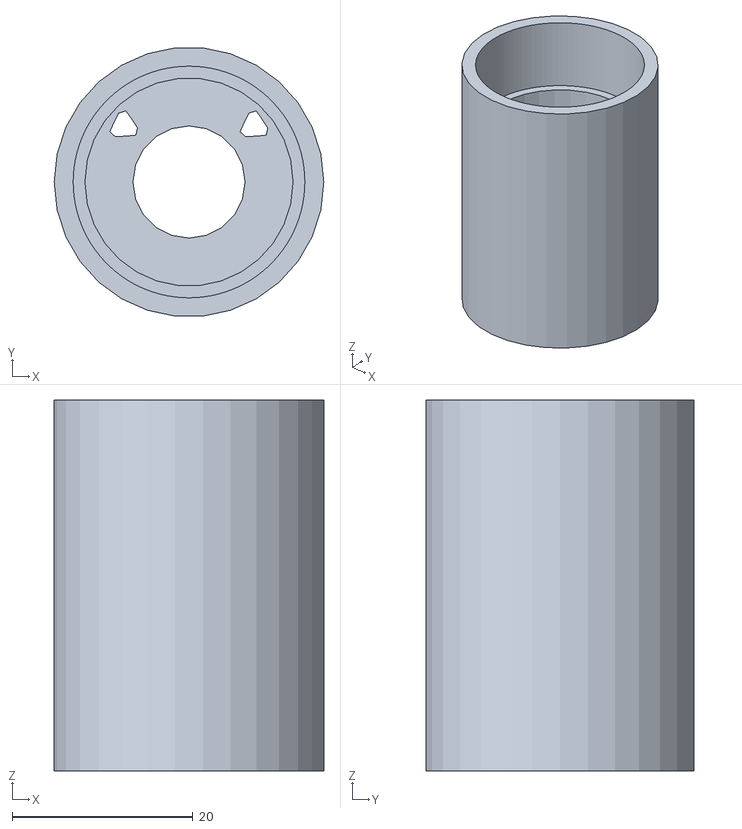
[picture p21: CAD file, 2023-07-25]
Phase 2 (Epifluorescence Microscope)/Hardware/Custom Epifluorescence Microscope Parts/STL/ModMicroTubeLens.stl
29.8 x 29.6 x 41.0

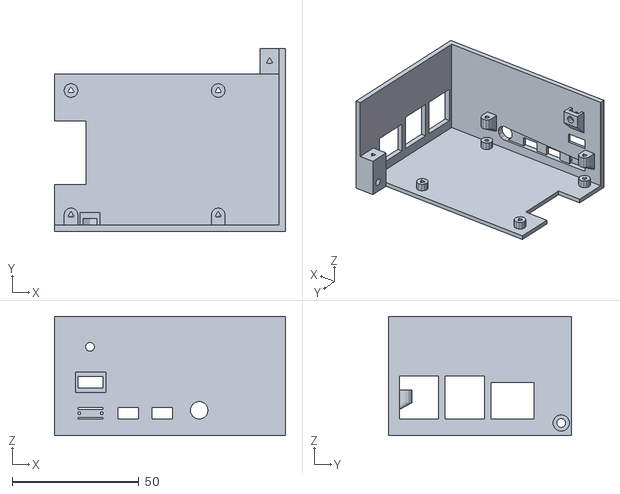
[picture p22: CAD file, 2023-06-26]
Phase 2 (Epifluorescence Microscope)/Hardware/Openflexure Parts_V7_V6/electronics_drawer.stl
91.0 x 72.0 x 47.0

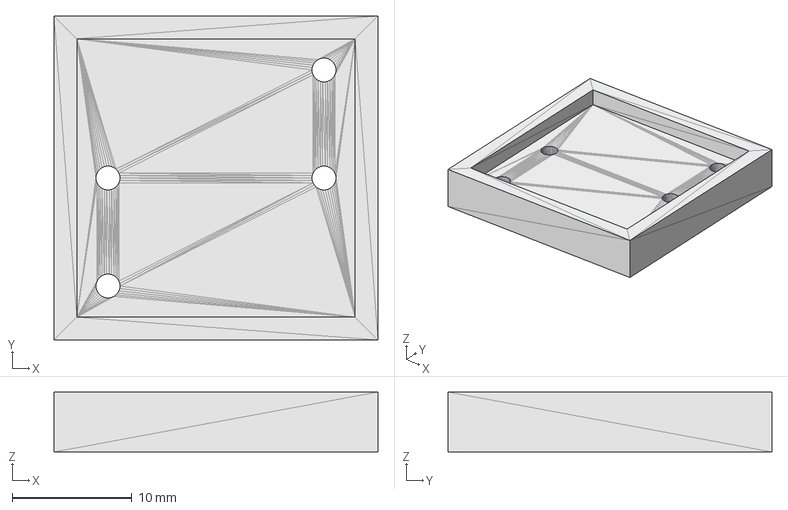
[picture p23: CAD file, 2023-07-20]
Modular Light Sources (ModLight)/ModLight/Common Files/STEP/Heatsink Drill Guide_STEP.step
27.0 x 27.0 x 5.00 mm

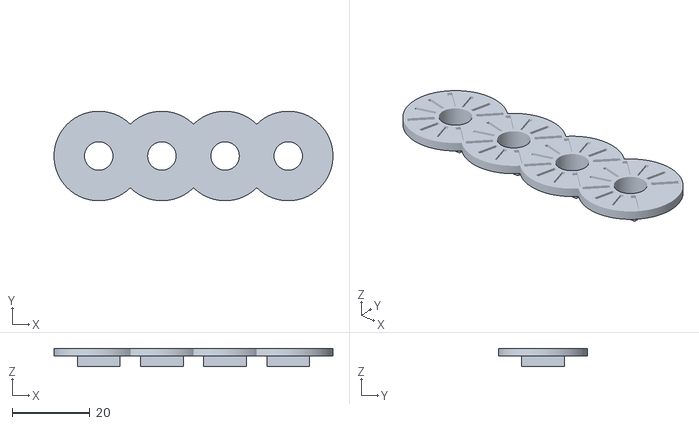
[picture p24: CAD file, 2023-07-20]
Modular Light Sources (ModLight)/ModLight/Electronics/STL/Scale Plate_STL.stl
71.7 x 23.0 x 4.70

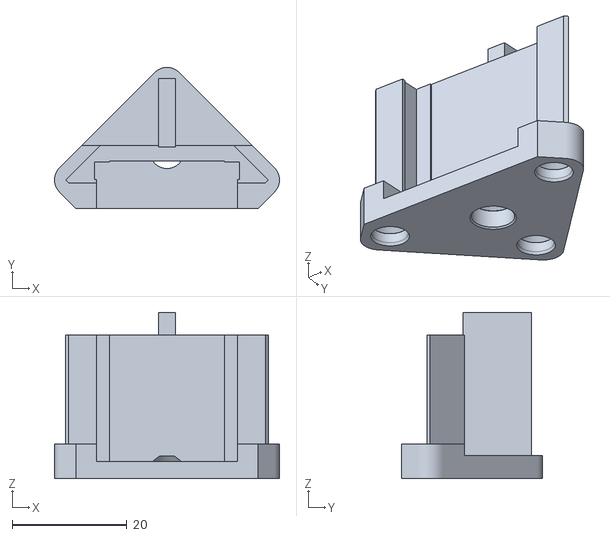
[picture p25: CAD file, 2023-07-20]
Modular Light Sources (ModLight)/ModLight/ModLight_Mirror/STL/MMirror Mount_STL.stl
39.2 x 24.6 x 29.0

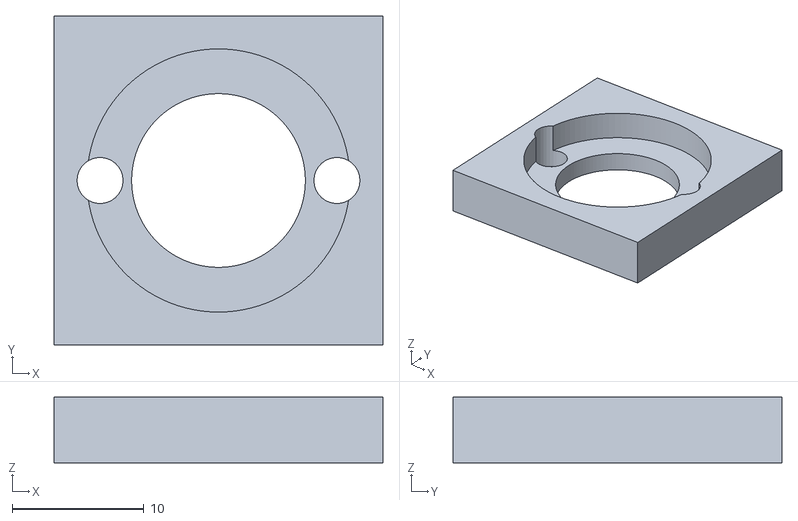
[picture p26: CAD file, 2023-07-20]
Modular Light Sources (ModLight)/ModLight/ModLight_XCube/STL/XLED Spacer_STL.stl
25.0 x 25.0 x 5.00

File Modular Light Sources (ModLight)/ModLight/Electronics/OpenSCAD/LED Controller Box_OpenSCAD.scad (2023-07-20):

module RGB_Base(){
difference(){
    union(){
minkowski(){
cube([95-5,62-5,10],center=true);
cylinder(d=5,h=0.01,$fn=80);    
}
hull(){
translate([41.5,35,-2.5])cylinder(d=12,h=5,$fn=80,center=true);
translate([41.5,-35,-2.5])cylinder(d=12,h=5,$fn=80,center=true);
}
hull(){
translate([-41.5,35,-2.5])cylinder(d=12,h=5,$fn=80,center=true);
translate([-41.5,-35,-2.5])cylinder(d=12,h=5,$fn=80,center=true);
}
}

translate([0,0,2])cube([89,56,10],center=true);
translate([0,25,8])cube([73,15,9],center=true);

translate([41.5,-35,-3])cylinder(d=4.4,h=7,$fn=80,center=true);
translate([-41.5,-35,-3])cylinder(d=4.4,h=7,$fn=80,center=true);
translate([41.5,35,-3])cylinder(d=4.4,h=7,$fn=80,center=true);
translate([-41.5,35,-3])cylinder(d=4.4,h=7,$fn=80,center=true);
}

difference(){
union(){
translate([75.241/2+1.5,45/2+0.2,-1])cylinder(d=7,h=6,$fn=80,center=true);
translate([-75.241/2+1.1,45/2-(30.449/2),-1])cylinder(d=7,h=6,$fn=80,center=true);
translate([-75.241/2+1.1,-45/2,-1])cylinder(d=7,h=6,$fn=80,center=true);
translate([75.241/2+1.5,-45/2,-1])cylinder(d=7,h=6,$fn=80,center=true);}

translate([75.241/2+1.5,45/2+0.2,-1])cylinder(d=2.8,h=7,$fn=80,center=true);
translate([-75.241/2+1.1,45/2-(30.449/2),-1])cylinder(d=2.8,h=7,$fn=80,center=true);
translate([-75.241/2+1.1,-45/2,-1])cylinder(d=2.8,h=7,$fn=80,center=true);
translate([75.241/2+1.5,-45/2,-1])cylinder(d=2.8,h=7,$fn=80,center=true);
}
}



module RGB_Thin_Dial(){
    difference(){
  cylinder(d1=14,d2=12,h=15,$fn=12);
  intersection(){
    translate([0,0,-2])cylinder(d=6.35,h=14,$fn=80);
    translate([0,0.75,5])cube([8,4.85,11],center=true);  
  }
    rotate([0,0,-90])translate([0,5,15])cube([1,10,2],center=true);      
    }
}



module Scale(){
rotate([0,0,45])translate([7.6,0,1.4])cube([6,1.1,2],center=true);
rotate([0,0,-45])translate([7.6,0,1.4])cube([6,1.1,2],center=true);
rotate([0,0,90+45])translate([7.6,0,1.4])cube([6,1.1,2],center=true);
rotate([0,0,-90-45])translate([7.6,0,1.4])cube([6,1.1,2],center=true);

rotate([0,0,45+90/3])translate([7.1,0,1.4])cube([5,0.8,2],center=true);
rotate([0,0,45+(90/3)*2])translate([7.1,0,1.4])cube([5,0.8,2],center=true);
rotate([0,0,(45+90/3)+90])translate([7.1,0,1.4])cube([5,0.8,2],center=true);
rotate([0,0,(45+(90/3)*2)+90])translate([7.1,0,1.4])cube([5,0.8,2],center=true);
rotate([0,0,-45-(90/3)*2])translate([7.1,0,1.4])cube([5,0.8,2],center=true);
rotate([0,0,-45-90/3])translate([7.1,0,1.4])cube([5,0.8,2],center=true);

}



module Dial_Plate(){
difference(){
union(){    
translate([0,0,-2.2])cube([11,11,3],center=true);
cylinder(d=23,h=2,$fn=100,center=true);
}
cylinder(d=7.3,h=10,$fn=100,center=true);

translate([6.5/2,-8.8/2,-3.5])cylinder(d=2,h=4,$fn=30,center=true);
translate([-6.5/2,8.8/2,-3.5])cylinder(d=2,h=4,$fn=30,center=true);
}
}



module Scale_Plate(){
    difference(){
union(){    
translate([0,0,-3])Dial_Plate();
translate([48.7/3,0,-3])Dial_Plate();
translate([(48.7/3)*2,0,-3])Dial_Plate();
translate([48.7,0,-3])Dial_Plate();
}
translate([0,0,-3])Scale();
translate([48.7/3,0,-3])Scale();
translate([(48.7/3)*2,0,-3])Scale();
translate([48.7,0,-3])Scale();
}
}



//RGB_Base();
//RGB_Thin_Dial();
translate([0,0,0])Scale_Plate();

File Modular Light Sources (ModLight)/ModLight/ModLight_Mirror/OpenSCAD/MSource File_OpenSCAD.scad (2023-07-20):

// Calibration Coefficients
// Ultimaker 2
A=1.001;
B=0.272;



module Light_Box(){
difference(){
union(){
// Mounting tabs    
hull(){
translate([50-5,25,-16])cylinder(d=16,h=8,$fn=80,center=true);
translate([-50-5,25,-16])cylinder(d=16,h=8,$fn=80,center=true);
}
hull(){
translate([50-5,-25,-16])cylinder(d=16,h=8,$fn=80,center=true);
translate([-50-5,-25,-16])cylinder(d=16,h=8,$fn=80,center=true);
}
// Overall enclosure
minkowski(){        
translate([-5,0,-3])cube([87,61,34],center=true);
cylinder(d=5,h=0.01,$fn=80,center=true);    
}
}
// Cutouts for LED assemblies
translate([-20.5,28,2.5])LED_Assembly_Cutout();
translate([-20.5,-28,2.5])rotate([0,0,180])LED_Assembly_Cutout();
translate([13.5,28,2.5])LED_Assembly_Cutout();
translate([13.5,-28,2.5])rotate([0,0,180])LED_Assembly_Cutout();

// Cutout for Fibre assembly
translate([-46,0,2.5])rotate([0,0,90])Fibre_Assembly_Cutout();

// Central recesses
translate([-3.5,0,4])cube([75,46,35],center=true);
translate([-3.5,0,3])cube([75,37,35],center=true);
translate([-3.5,0,13.5])cube([77,48,2],center=true);

// Kinematic mount cutouts
translate([13.5,0,-16.5])Pin_Magnet_Cutouts();
translate([-20.5,0,-16.5])Pin_Magnet_Cutouts();

// Locating magnets for lid
translate([39-2,29,13])cylinder(d=2.97*A+B,h=2.2,$fn=80,center=true);
translate([39-2,-29,13])cylinder(d=2.97*A+B,h=2.2,$fn=80,center=true);
translate([-49+2,29,13])cylinder(d=2.97*A+B,h=2.2,$fn=80,center=true);
translate([-49+2,-29,13])cylinder(d=2.97*A+B,h=2.2,$fn=80,center=true);

// Mounting tab holes and screw recesses
translate([50-5,25,-15])cylinder(d=6.3,h=11,$fn=80,center=true);
translate([-50-5,25,-15])cylinder(d=6.3,h=11,$fn=80,center=true);
translate([50-5,-25,-15])cylinder(d=6.3,h=11,$fn=80,center=true);
translate([-50-5,-25,-15])cylinder(d=6.3,h=11,$fn=80,center=true);
translate([50-5,25,0])cylinder(d1=11,d2=7.6,h=33,$fn=80,center=true);
translate([-50-5,25,0])cylinder(d1=11,d2=7.6,h=33,$fn=80,center=true);
translate([50-5,-25,0])cylinder(d1=11,d2=7.6,h=33,$fn=80,center=true);
translate([-50-5,-25,0])cylinder(d1=11,d2=7.6,h=33,$fn=80,center=true);
}
}



module Pin_Magnet_Cutouts(){
translate([-10.6,-10.6,0])rotate([0,0,90])pins();
translate([10.6,-10.6,0])rotate([0,0,45])pins();
translate([10.6,10.6,0])rotate([0,0,-45])pins();
translate([-10.6,10.6,0])rotate([0,0,90])pins();
translate([3.5,3.5,0.7])cylinder(d=5.95*A+B,h=3,center=true,$fn=100); // Indent for magnet
translate([3.5,-3.5,0.7])cylinder(d=5.95*A+B,h=3,center=true,$fn=100); // Indent for magnet  
}



module Pin_Magnet_Model(){
translate([-10.6,-10.6-2.3,0])rotate([0,90,0])cylinder(d=2,h=8,$fn=50,center=true);
translate([-10.6,-10.6+2.3,0])rotate([0,90,0])cylinder(d=2,h=8,$fn=50,center=true);
translate([10.6,-10.6,0])rotate([0,0,-45])union(){    
translate([0,-2.3,0])rotate([0,90,0])cylinder(d=2,h=8,$fn=50,center=true);
translate([0,+2.3,0])rotate([0,90,0])cylinder(d=2,h=8,$fn=50,center=true);
}
translate([10.6,10.6,0])rotate([0,0,45])union(){    
translate([0,-2.3,0])rotate([0,90,0])cylinder(d=2,h=8,$fn=50,center=true);
translate([0,+2.3,0])rotate([0,90,0])cylinder(d=2,h=8,$fn=50,center=true);
}
translate([-10.6,10.6-2.3,0])rotate([0,90,0])cylinder(d=2,h=8,$fn=50,center=true);
translate([-10.6,10.6+2.3,0])rotate([0,90,0])cylinder(d=2,h=8,$fn=50,center=true);
translate([3.5,3.5,-0.7])cylinder(d=5.95*A+B,h=3,center=true,$fn=100); // Indent for magnet
translate([3.5,-3.5,-0.7])cylinder(d=5.95*A+B,h=3,center=true,$fn=100); // Indent for magnet  
}



module Light_Box_Lid(){
difference(){    

// Overall Lid Envelope
union(){    
minkowski(){        
translate([-5,0,-5])cube([87,61,6],center=true);
cylinder(d=5,h=0.01,$fn=80,center=true);    
}
translate([-3.5,0,-8])cube([76.2,47.2,2],center=true);
}

// Recess
translate([-3.5,0,-7.5])cube([74,45,4],center=true);

// Magnets for lid
translate([39-2,29,-7])cylinder(d=2.97*A+B,h=2.2,$fn=80,center=true);
translate([39-2,-29,-7])cylinder(d=2.97*A+B,h=2.2,$fn=80,center=true);
translate([-49+2,29,-7])cylinder(d=2.97*A+B,h=2.2,$fn=80,center=true);
translate([-49+2,-29,-7])cylinder(d=2.97*A+B,h=2.2,$fn=80,center=true);

// Cutouts for LED assemblies
translate([-20.5,28,-26+1.6])rotate([0,0,90])cube([5.7,30.7,36],center=true);
translate([-20.5,-28,-26+1.6])rotate([0,0,90])cube([5.7,30.7,36],center=true);
translate([13.5,28,-26+1.6])rotate([0,0,90])cube([5.7,30.7,36],center=true);
translate([13.5,-28,-26+1.6])rotate([0,0,90])cube([5.7,30.7,36],center=true);

translate([-20.5,24,-10.6])rotate([0,0,90])cube([5.7,29.2,5],center=true);
translate([-20.5,-24,-10.6])rotate([0,0,90])cube([5.7,29.2,5],center=true);
translate([13.5,24,-10.6])rotate([0,0,90])cube([5.7,29.2,5],center=true);
translate([13.5,-24,-10.6])rotate([0,0,90])cube([5.7,29.2,5],center=true);

// Cutout for Fibre assembly
translate([-46,0,-26+1.6])cube([5.7,30.7,36],center=true);
}
}



module Mirror(){
difference(){
union(){        
rotate([0,0,45])cube([25,25,25],center=true);
minkowski(){    
translate([0,0,-9.5])rotate([0,0,45])cube([23.5,23.5,6],center=true);
cylinder(d=6,h=0.01,$fn=80,center=true);    
}    
}
translate([0,1.58,3])cube([25.2,3.05,25],center=true);
translate([0,1.8,3])cube([20,3,25],center=true);
translate([0,0.55-2,3.5])cube([24.6,9.1,26],center=true);
translate([0,-15,0])cube([36,20,36],center=true);
translate([0,-10.5,6.005])cube([36,20,25],center=true);
translate([0,16,4.005])cube([36,20,25],center=true);
translate([0,15,-12.3])rotate([0,180,0])bearing();
translate([15,0,-12.3])rotate([0,180,0])bearing();
translate([-15,0,-12.3])rotate([0,180,0])bearing();
rotate([0,0,45])translate([3.5,3.5,-12.3])cylinder(d2=5*A+B,d1=7*A+B,h=1,center=true,$fn=150);
rotate([0,0,45])translate([3.5,3.5,-11.1])cylinder(d=5.95*A+B,h=3,center=true,$fn=100); // Indent for magnet
rotate([0,0,45])translate([3.5,3.5,-9.1])cylinder(d2=3.8*A+B,d1=5.95*A+B,h=1.1,center=true,$fn=100);
}
translate([0,11.7,3.95])cube([3,12,25],center=true);
//color("lightgrey",0.9)translate([0,1.58,3])cube([25.2,3.05,25],center=true);
}



module Heatsink_Drill_Guide(){    
    difference(){
    cube([27,27,5],center=true);
    translate([0,0,2])cube([23.2,23.2,3],center=true);    
    translate([18/2,0,0])cylinder(d=2,h=7,$fn=30,center=true);
    translate([-18/2,0,0])cylinder(d=2,h=7,$fn=30,center=true);
    translate([18/2,18/2,0])cylinder(d=2,h=7,$fn=30,center=true);
    translate([-18/2,-18/2,0])cylinder(d=2,h=7,$fn=30,center=true);    
    }  
}



module Heatsink_Mount_C(){    
    difference(){
    cube([30,5,30],center=true);
    translate([0,1.8,0])cube([23.2,5,23.2],center=true);    
    translate([0,0,0])rotate([90,0,0])cylinder(d=21,h=7,$fn=100,center=true);
    translate([18/2,0,0])rotate([90,0,0])cylinder(d=3.5,h=7,$fn=30,center=true);
    translate([-18/2,0,0])rotate([90,0,0])cylinder(d=3.5,h=7,$fn=30,center=true);
    translate([18/2,0,-18/2])rotate([90,0,0])cylinder(d=2.5,h=7,$fn=30,center=true);
    translate([-18/2,0,18/2])rotate([90,0,0])cylinder(d=2.5,h=7,$fn=30,center=true);     
    }  
}



module Heatsink_Mount_R(){    
    difference(){
    cube([30,5,30],center=true);
    translate([0,1.8,0])cube([23.2,5,23.2],center=true);    
    //#translate([0,0,0])rotate([90,0,0])cylinder(d=21,h=7,$fn=100,center=true);
    translate([0,0,0])cube([23.2,7,14],center=true);
    translate([18/2,0,0])rotate([90,0,0])cylinder(d=3.5,h=7,$fn=30,center=true);
    translate([-18/2,0,0])rotate([90,0,0])cylinder(d=3.5,h=7,$fn=30,center=true);
    translate([18/2,0,-18/2])rotate([90,0,0])cylinder(d=2.5,h=7,$fn=30,center=true);
    translate([-18/2,0,18/2])rotate([90,0,0])cylinder(d=2.5,h=7,$fn=30,center=true);     
    }  
}



module PMMA_Mount(){    
    difference(){
    translate([0,-1.5,0])cube([26.2,8,26.2],center=true);
    translate([0,-1.3,0])rotate([90,0,0])cylinder(d1=13*A+B+0.15,d2=13*A+B-0.15,h=7,$fn=200,center=true);     
    rotate([90,0,0])cylinder(d=12.2,h=12,$fn=100,center=true);
    translate([0,3,0])rotate([90,0,0])cylinder(d=18,h=5,$fn=100,center=true);    
    translate([18/2,3.5,0])rotate([90,0,0])cylinder(d=6,h=7,$fn=50,center=true);
    translate([-18/2,3.5,0])rotate([90,0,0])cylinder(d=6,h=7,$fn=50,center=true);    
    translate([-18/2,0,18/2])rotate([90,0,0])cylinder(d=3,h=12,$fn=30,center=true);
    translate([18/2,0,-18/2])rotate([90,0,0])cylinder(d=3,h=12,$fn=30,center=true);
    translate([5.5,2.5,10])cylinder(d=3,h=20,$fn=30,center=true);
    translate([-5.5,2.5,10])cylinder(d=3,h=20,$fn=30,center=true);
    translate([0,-4.3,0])rotate([90,0,0])cylinder(d=13*A+B,h=1,$fn=200,center=true);    
    }  
}
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

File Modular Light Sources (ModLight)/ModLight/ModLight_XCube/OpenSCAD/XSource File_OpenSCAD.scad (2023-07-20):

// Calibration Coefficients
// Ultimaker 2
A=1.001;
B=0.272;



module Light_Mixer_Base(){
difference(){
union(){
// Mounting tabs    
hull(){
translate([50-12.5,25,-16])cylinder(d=16,h=8,$fn=80,center=true);
translate([-25-12.5,25,-16])cylinder(d=16,h=8,$fn=80,center=true);
}
hull(){
translate([50-12.5,-25,-16])cylinder(d=16,h=8,$fn=80,center=true);
translate([-25-12.5,-25,-16])cylinder(d=16,h=8,$fn=80,center=true);
}
// Overall enclosure
minkowski(){        
translate([0,0,-3])cube([61,61,34],center=true);
cylinder(d=5,h=0.01,$fn=80,center=true);    
}
}
// Cutouts for LED assemblies
translate([0,28,2.5])LED_Assembly_Cutout();
translate([0,-28,2.5])rotate([0,0,180])LED_Assembly_Cutout();
translate([28,0,2.5])rotate([0,0,-90])LED_Assembly_Cutout();

// Cutout for Fibre assembly
translate([-28,0,2.5])rotate([0,0,90])Fibre_Assembly_Cutout();

// Central recesses
translate([0,0,6])cube([45,46,35],center=true);
translate([0,0,13.5])cube([48,48,2],center=true);

// Locating magnets for lid
translate([29,29,13])cylinder(d=2.97*A+B,h=2.2,$fn=80,center=true);
translate([29,-29,13])cylinder(d=2.97*A+B,h=2.2,$fn=80,center=true);
translate([-29,29,13])cylinder(d=2.97*A+B,h=2.2,$fn=80,center=true);
translate([-29,-29,13])cylinder(d=2.97*A+B,h=2.2,$fn=80,center=true);

// Mounting tab holes and screw recesses
translate([50-12.5,25,-15])cylinder(d=6.3,h=11,$fn=80,center=true);
translate([-25-12.5,25,-15])cylinder(d=6.3,h=11,$fn=80,center=true);
translate([50-12.5,-25,-15])cylinder(d=6.3,h=11,$fn=80,center=true);
translate([-25-12.5,-25,-15])cylinder(d=6.3,h=11,$fn=80,center=true);
translate([50-12.5,25,0])cylinder(d1=11,d2=7.6,h=33,$fn=80,center=true);
translate([-25-12.5,25,0])cylinder(d1=11,d2=7.6,h=33,$fn=80,center=true);
translate([50-12.5,-25,0])cylinder(d1=11,d2=7.6,h=33,$fn=80,center=true);
translate([-25-12.5,-25,0])cylinder(d1=11,d2=7.6,h=33,$fn=80,center=true);

// Recess for X-Cube
translate([0,0,-1])cube([24.9,24.9,24.8],center=true);
}
}



module X_Prism(){
// X-Cube
color([0.7,1,1,0.4])translate([0,0,-1])cube([24.8,24.8,24.8],center=true);
color("blue")rotate([0,0,-45])cube([35,0.3,23],center=true);
color("red")rotate([0,0,45])cube([35,0.3,23],center=true);     
}



module Light_Mixer_Lid(){
difference(){    

// Overall Lid Envelope
union(){    
minkowski(){        
translate([0,0,-5])cube([61,61,6],center=true);
cylinder(d=5,h=0.01,$fn=80,center=true);    
}
translate([0,0,-8])cube([47.2,47.2,2],center=true);
}

// Recess
translate([0,0,-7.5])cube([45,45,4],center=true);

// Magnets for lid
translate([29,29,-7])cylinder(d=2.97*A+B,h=2.2,$fn=80,center=true);
translate([29,-29,-7])cylinder(d=2.97*A+B,h=2.2,$fn=80,center=true);
translate([-29,29,-7])cylinder(d=2.97*A+B,h=2.2,$fn=80,center=true);
translate([-29,-29,-7])cylinder(d=2.97*A+B,h=2.2,$fn=80,center=true);

// Cutouts for LED assemblies
translate([0,28,-26+1.6])rotate([0,0,90])cube([5.7,30.7,36],center=true);
translate([0,-28,-26+1.6])rotate([0,0,90])cube([5.7,30.7,36],center=true);
translate([28,0,-26+1.6])cube([5.7,30.7,36],center=true);
translate([0,24,-10.6])rotate([0,0,90])cube([5.7,29.2,5],center=true);
translate([0,-24,-10.6])rotate([0,0,90])cube([5.7,29.2,5],center=true);
translate([23,0,-10.6])rotate([0,0,0])cube([5.7,29.2,5],center=true);

// Cutout for Fibre assembly
translate([-28,0,-26+1.6])cube([5.7,30.7,36],center=true);
translate([-23,0,-10.6])rotate([0,0,0])cube([5.7,29.2,5],center=true);
}
}



module Heatsink_Drill_Guide(){    
    difference(){
    cube([27,27,5],center=true);
    translate([0,0,2])cube([23.2,23.2,3],center=true);    
    translate([18/2,0,0])cylinder(d=2,h=7,$fn=30,center=true);
    translate([-18/2,0,0])cylinder(d=2,h=7,$fn=30,center=true);
    translate([18/2,18/2,0])cylinder(d=2,h=7,$fn=30,center=true);
    translate([-18/2,-18/2,0])cylinder(d=2,h=7,$fn=30,center=true);    
    }  
}



module Heatsink_Mount_C(){    
    difference(){
    cube([30,5,30],center=true);
    translate([0,1.8,0])cube([23.2,5,23.2],center=true);    
    translate([0,0,0])rotate([90,0,0])cylinder(d=21,h=7,$fn=100,center=true);
    translate([18/2,0,0])rotate([90,0,0])cylinder(d=3.5,h=7,$fn=30,center=true);
    translate([-18/2,0,0])rotate([90,0,0])cylinder(d=3.5,h=7,$fn=30,center=true);
    translate([18/2,0,-18/2])rotate([90,0,0])cylinder(d=2.5,h=7,$fn=30,center=true);
    translate([-18/2,0,18/2])rotate([90,0,0])cylinder(d=2.5,h=7,$fn=30,center=true);     
    }  
}



module Heatsink_Mount_R(){    
    difference(){
    cube([30,5,30],center=true);
    translate([0,1.8,0])cube([23.2,5,23.2],center=true);   
    translate([0,0,0])cube([23.2,7,14],center=true);
    translate([18/2,0,0])rotate([90,0,0])cylinder(d=3.5,h=7,$fn=30,center=true);
    translate([-18/2,0,0])rotate([90,0,0])cylinder(d=3.5,h=7,$fn=30,center=true);
    translate([18/2,0,-18/2])rotate([90,0,0])cylinder(d=2.5,h=7,$fn=30,center=true);
    translate([-18/2,0,18/2])rotate([90,0,0])cylinder(d=2.5,h=7,$fn=30,center=true);     
    }  
}



module LED_Spacer(){    
    difference(){
    cube([25,25,5],center=true);
    translate([0,0,3])cylinder(d=20,h=7,$fn=100,center=true);   
    translate([0,0,0])cylinder(d=13.2,h=7,$fn=100,center=true); 
    translate([18/2,0,0])cylinder(d=3.5,h=7,$fn=30,center=true);
    translate([-18/2,0,0])cylinder(d=3.5,h=7,$fn=30,center=true);    
    }  
}



module PMMA_Mount(){    
    difference(){
    translate([0,-1.5,0])cube([26.2,8,26.2],center=true);
    translate([0,-1.3,0])rotate([90,0,0])cylinder(d1=13*A+B+0.15,d2=13*A+B-0.15,h=7,$fn=200,center=true);     
    rotate([90,0,0])cylinder(d=12.2,h=12,$fn=100,center=true);
    translate([0,3,0])rotate([90,0,0])cylinder(d=18,h=5,$fn=100,center=true);    
    translate([18/2,3.5,0])rotate([90,0,0])cylinder(d=6,h=7,$fn=50,center=true);
    translate([-18/2,3.5,0])rotate([90,0,0])cylinder(d=6,h=7,$fn=50,center=true);    
    translate([-18/2,0,18/2])rotate([90,0,0])cylinder(d=3,h=12,$fn=30,center=true);
    translate([18/2,0,-18/2])rotate([90,0,0])cylinder(d=3,h=12,$fn=30,center=true);
    translate([5.5,2.5,10])cylinder(d=3,h=20,$fn=30,center=true);
    translate([-5.5,2.5,10])cylinder(d=3,h=20,$fn=30,center=true);
    translate([0,-4.3,0])rotate([90,0,0])cylinder(d=13*A+B,h=1,$fn=200,center=true);    
    }  
}



module Fibre_Mount(){    
    difference(){
    cube([30,5,30],center=true);
            
    translate([0,1.5,0])rotate([90,0,0])cylinder(d1=13.3,d2=13.05,h=7,$fn=200,center=true);     
    
    rotate([90,0,0])cylinder(d=12.2,h=12,$fn=100,center=true); 
    
    translate([0,-1.5,0])rotate([90,0,0])cylinder(d=13.15,h=1,$fn=200,center=true); 
        
    translate([19/2,0,19/2])rotate([90,0,0])cylinder(d=2,h=7,$fn=30,center=true);
    translate([-19/2,0,-19/2])rotate([90,0,0])cylinder(d=2,h=7,$fn=30,center=true);
    translate([-19/2,0,19/2])rotate([90,0,0])cylinder(d=2,h=12,$fn=30,center=true);
    translate([19/2,0,-19/2])rotate([90,0,0])cylinder(d=2,h=12,$fn=30,center=true);    
    }  
}



module Fibre_Holder(){    
    difference(){
    union(){    
    minkowski(){    
    cube([21.5,5,21.5],center=true);
    rotate([90,0,0])cylinder(d=5,h=0.01,$fn=50,center=true);        
    }
    translate([0,5,0])rotate([90,0,0])cylinder(d2=10,d1=8,h=14,$fn=100,center=true); 
} 
    translate([0,6,0])rotate([90,0,0])cylinder(d=3.32*A+B,h=14,$fn=80,center=true);

    translate([0,-2.5,0])rotate([90,0,0])cylinder(d1=2.5,d2=8,h=3,$fn=80,center=true);

    rotate([90,0,0])cylinder(d=2.5,h=10,$fn=80,center=true);     
        
    translate([19/2,0,19/2])rotate([90,0,0])cylinder(d=3.5,h=7,$fn=50,center=true);
    translate([-19/2,0,-19/2])rotate([90,0,0])cylinder(d=3.5,h=7,$fn=50,center=true);
    translate([-19/2,0,19/2])rotate([90,0,0])cylinder(d=3.5,h=12,$fn=50,center=true);
    translate([19/2,0,-19/2])rotate([90,0,0])cylinder(d=3.5,h=12,$fn=50,center=true);    
    }  
}



module Fibre_Collimator(){
  difference(){
 
union(){
    translate([0,-3,0])rotate([90,0,0])cylinder(d=17,h=8,$fn=170,center=true);
    translate([0,5,0])rotate([90,0,0])cylinder(d2=14,d1=8,h=14,$fn=120,center=true); 
    
}  
    translate([0,7.6,0])rotate([90,0,0])cylinder(d=3.1*A+B,h=14,$fn=80,center=true);
    translate([0,-2.5,0])rotate([90,0,0])cylinder(d1=2.4,d2=13.4,h=6.5,$fn=120,center=true);
    rotate([90,0,0])cylinder(d=2.5,h=10,$fn=80,center=true);        
translate([0,-6.7,0])rotate([90,0,0])cylinder(d=13.22,h=2,$fn=200,center=true);
translate([0,-7.25,0])rotate([90,0,0])cylinder(d1=12.2,d2=16,h=2,$fn=200,center=true);
    }     
}
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

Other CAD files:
Modular Light Sources (ModLight)/ModLight/Common Files/STL/PMMA Mount_STL.stl
Modular Light Sources (ModLight)/ModLight/ModLight_XCube/STEP/XLight Mixer (Lid)_STEP.step
Modular Light Sources (ModLight)/ModLight/OpenFlexure_Modified/Condenser_Holder_Modified.stl
Phase 2 (Epifluorescence Microscope)/Hardware/Custom Epifluorescence Microscope Parts/STL/Illumination_Modified.stl
Phase 2 (Epifluorescence Microscope)/Hardware/Custom Epifluorescence Microscope Parts/OpenSCAD/Base1.scad
Modular Light Sources (ModLight)/ModLight/Common Files/STEP/Fibre Holder_STEP.step
Modular Light Sources (ModLight)/ModLight/Common Files/STEP/Heatsink Mount_STEP.step
Modular Light Sources (ModLight)/ModLight/Common Files/STEP/PMMA Mount_STEP.step
Modular Light Sources (ModLight)/ModLight/Common Files/STL/Fibre Holder_STL.stl
Modular Light Sources (ModLight)/ModLight/Common Files/STL/Fibre Mount_STL.stl
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

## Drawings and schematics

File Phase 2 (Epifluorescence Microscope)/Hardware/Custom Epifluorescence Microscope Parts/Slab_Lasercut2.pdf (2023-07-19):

# C:/Users/rober/OneDrive/Desktop/ModMicro/modmicroopenscad/Slab_Lasercut2.scad

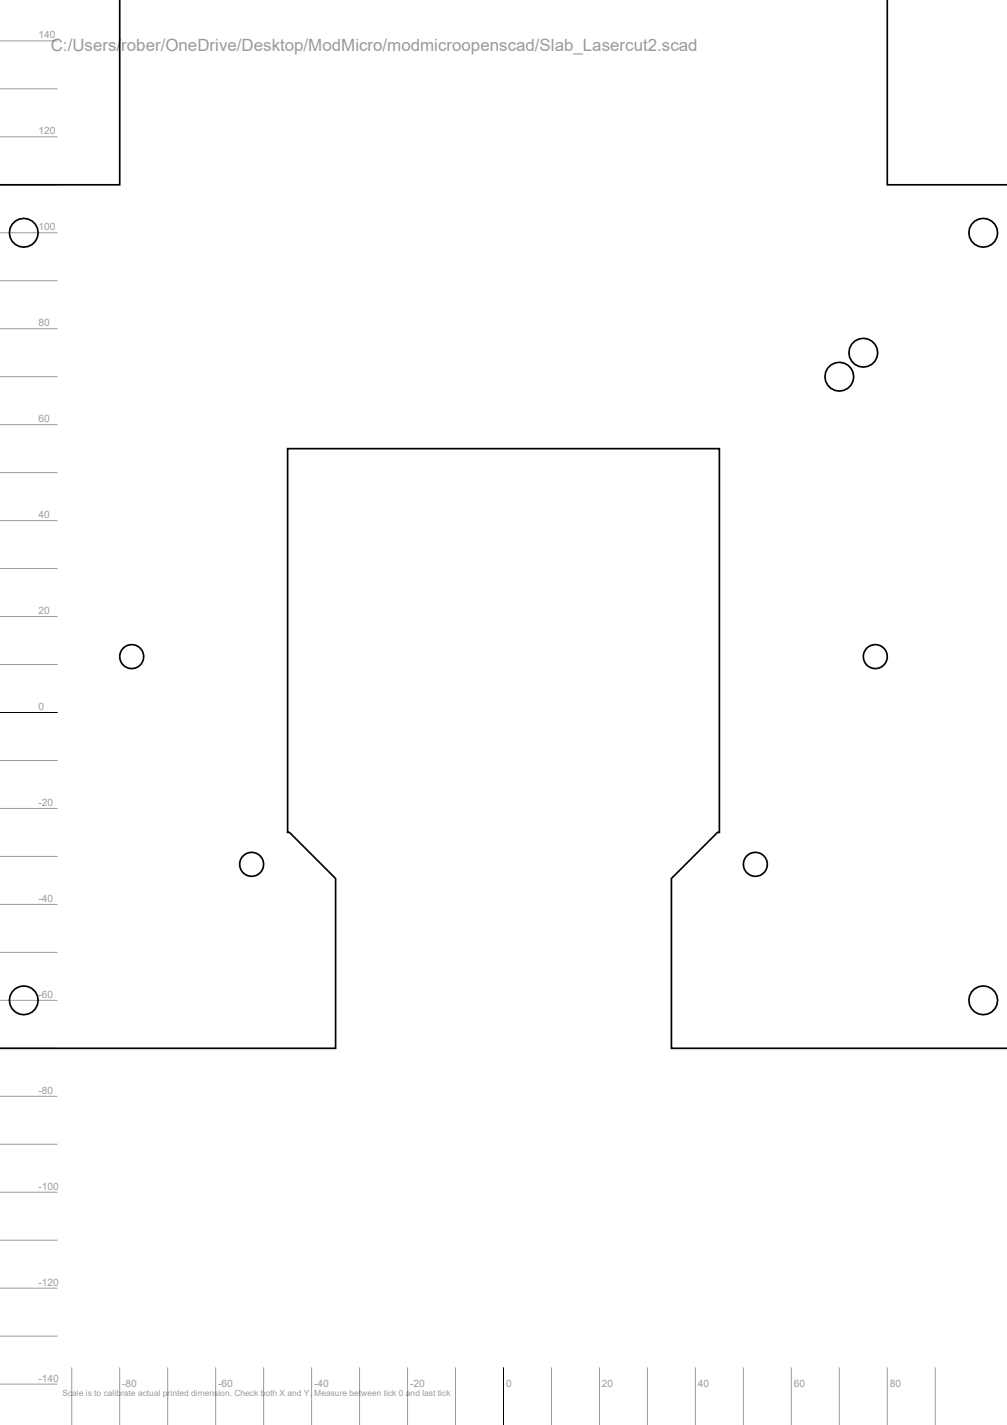
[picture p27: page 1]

Scale is to calibrate actual printed dimension. Check both X and Y. Measure between tick 0 and last tick

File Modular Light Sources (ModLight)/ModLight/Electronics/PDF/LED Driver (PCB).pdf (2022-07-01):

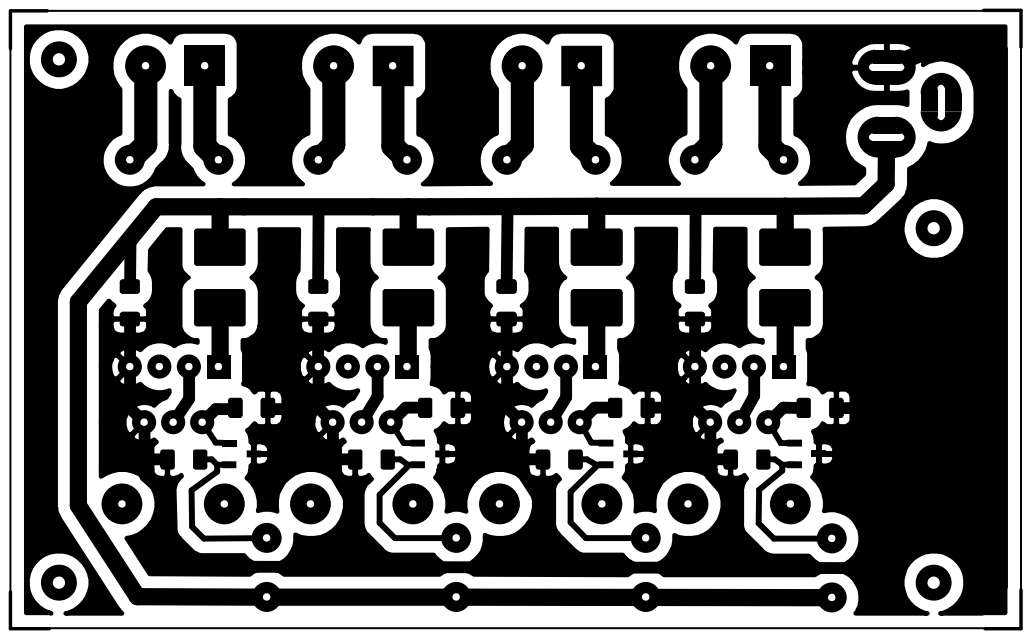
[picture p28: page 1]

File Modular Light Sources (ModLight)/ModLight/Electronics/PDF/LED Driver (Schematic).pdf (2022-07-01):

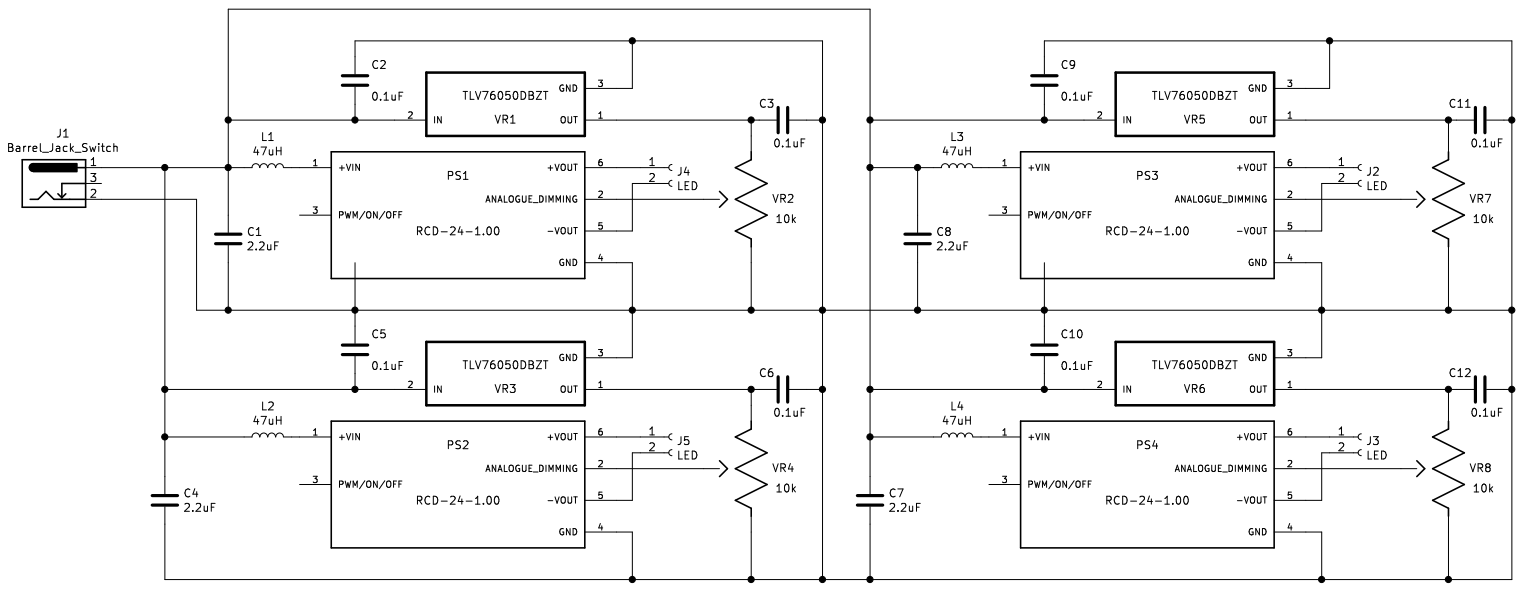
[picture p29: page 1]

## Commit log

2021-12-09 Sharpening algorithm update v1.0
    Sharpening algorithm with sample data from Harriet Bishop (v1.0)
2021-12-09 Epifluorescence Microscopy
    Modified OpenFlexure microscope for access to optics, light and filter controls for epifluorescence imaging
2022-10-17 Delete ModLight/design-files-and-bill-of-materials-1 directory
    Updating folder to latest version
    [Bill of Materials.xlsx, Fibre Collimator.stl, Fibre Holder.stl, Fibre Mount.stl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]
2022-10-17 Version 2 Update
    Files added to the repository, following final revision submission
    Design files and Bill of Materials for version 2 of ModLight
    [Bill of Materials.xlsx, Condenser_Holder_Modified.stl, Dial_STL.stl, Fibre Collimator_STL.stl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]
2022-12-07 Updated files (Zenodo and HardwareX)
    Updated files, as of the version available through HardwareX publication and on Zenodo (https://zenodo.org/record/7385903)
    [Condenser_Holder_Modified.stl, Dial_STL.stl, Fibre Collimator_STL.stl, Fibre Holder_STEP.step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]
2023-06-26 Epi microscope parts committed and added to Git
    [Base1.scad, Base1.stl, Bill of Materials.xlsx, Cube1_mirror.scad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]
2023-07-18 Bill of Materials updated
    [Bill of Materials.xlsx]
2023-07-19 Laser-cut slabs and pedestal posts openscad stl files
    [Pedestal_posts.scad, Pedestal_posts.stl, Slab_Lasercut2.scad]
2023-07-20 Folders moved
    [Bill of Materials.xlsx, Condenser_Holder_Modified.stl, Dial_STL.stl, Fibre Collimator_STL.stl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]
2023-07-25 Files updated
    [Illumination_Modified.scad, Illumination_Modified.stl, ModMicroTubeLens.scad, ModMicroTubeLens.stl]
